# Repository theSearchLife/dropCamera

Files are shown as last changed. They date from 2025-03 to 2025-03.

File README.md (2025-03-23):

# Hardware

## Burnwire mechanism

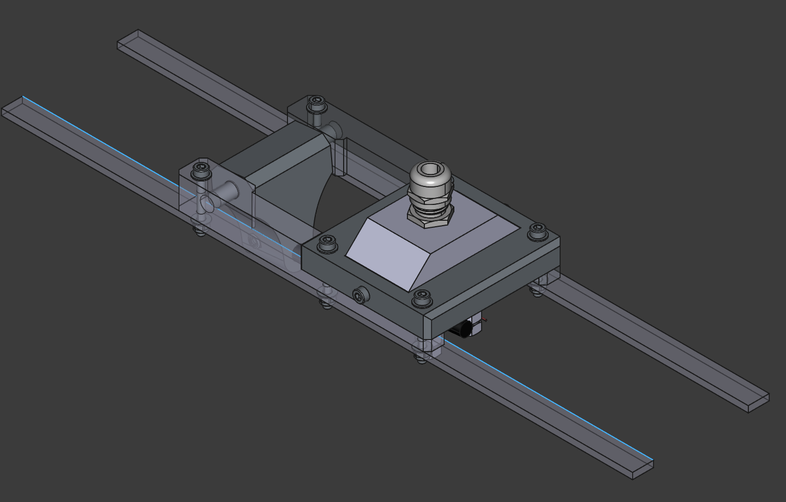
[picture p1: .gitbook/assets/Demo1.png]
Demo

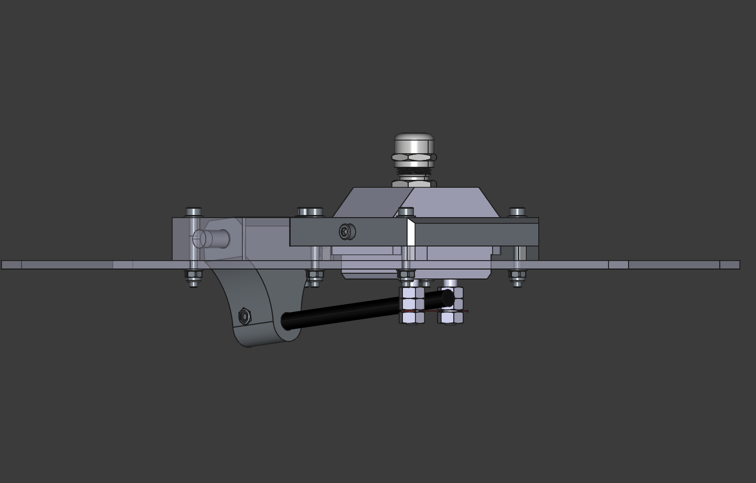
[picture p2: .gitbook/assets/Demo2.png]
Demo

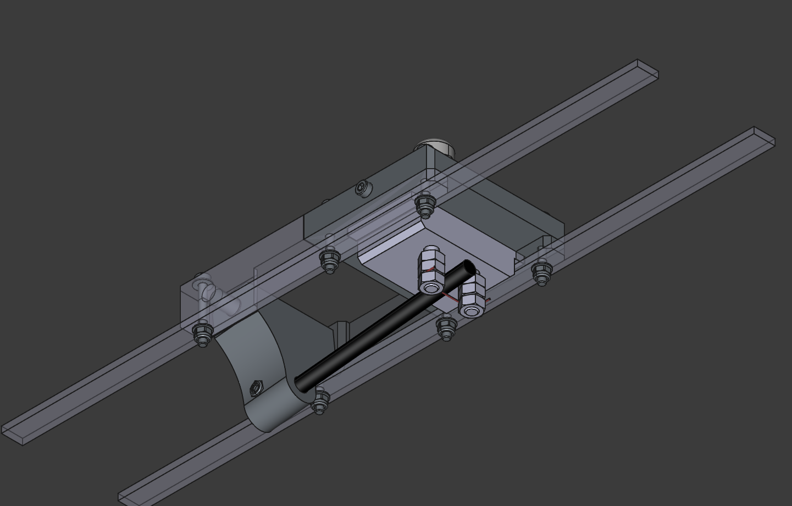
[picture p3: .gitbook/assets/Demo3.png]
Demo

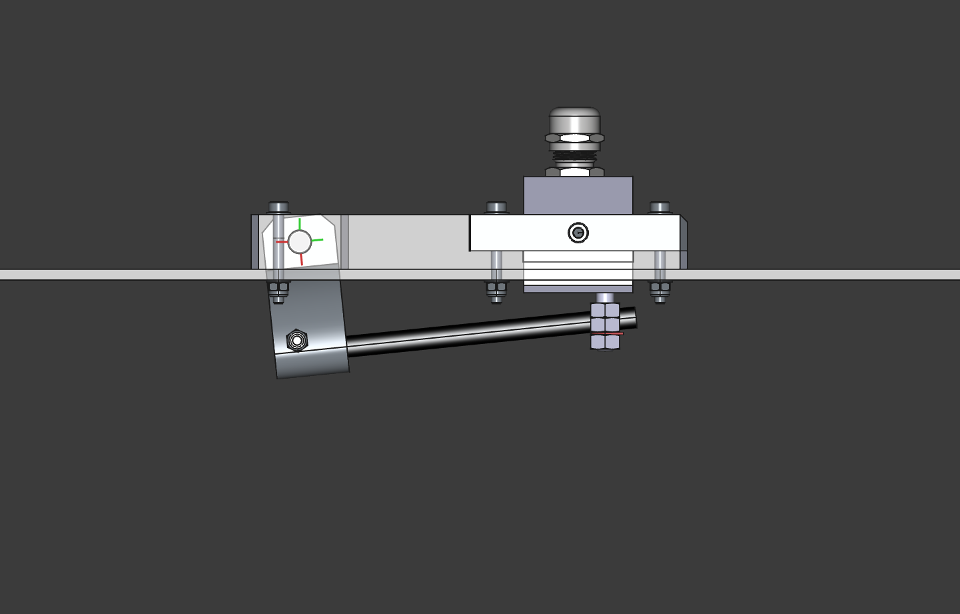
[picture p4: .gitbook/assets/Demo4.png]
Demo

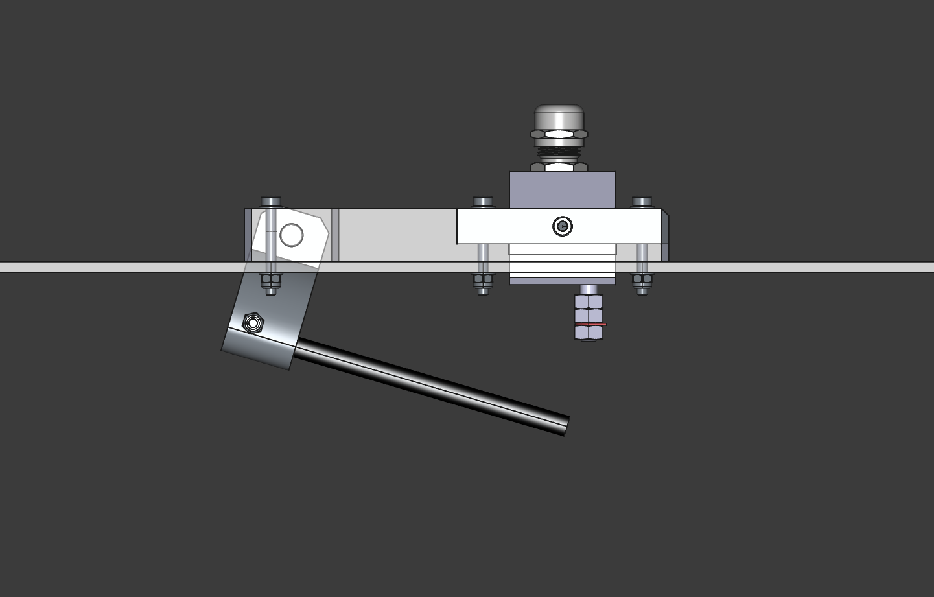
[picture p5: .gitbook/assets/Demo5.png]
Demo


### Hardware BOM

**All rods and fasteners must be stainless steel 316/A4**

* Rod 6x55mm
* Rod 6x70mm
* M12 Cable gland
* 2x Ring terminals
* 2x M5x25 ISO4017, [DIN 933 ](https://accu-components.com/us/full-thread-hexagon-bolts/19162-SEBF-M5-25-A4)  Screw (Hexagon head)
* 8x M5 nut [DIN 934](https://accu-components.com/us/hexagon-nuts/7910-HPN-M5-A4)
* 2x M5 [Star Washer](https://accu-components.com/us/external-fine-tooth-locking-washers/63131-HLFW-M5-A4)
* 7x M3 [DIN 985](https://accu-components.com/us/hexagon-nylon-locking-nuts/7957-HNN-M3-A4) (Nylon lock nut)
* 2x M3 nut [DIN 934](https://accu-components.com/us/hexagon-nuts/7907-HPN-M3-A4)
* 12x M3 Washer [DIN 125](https://accu-components.com/us/metric-flat-washers/72508-HPW-M3-A4)
  * Optional replace 6x M3 spring washers [DIN127B](https://accu-components.com/us/rectangular-profile-spring-washers/62558-HRSW-M3-A4)
* 2x M3x10 [DIN 912](https://accu-components.com/us/metric-cap-head-screws/3975-SSCF-M3-10-A4), DIN7984 or ISO4762 (Socket Head)
* M3x12 [DIN 912](https://accu-components.com/us/metric-cap-head-screws/3976-SSCF-M3-12-A4), DIN7984 or ISO4762 (Socket Head)
* 6x M3x25 [DIN 912](https://accu-components.com/us/metric-cap-head-screws/642040-SSCF-M3-25-A4), DIN7984 or ISO4762 (Socket Head)

* Nichromium wire

### 3D printing 

**Parts**
* BurnwireHolder
* BurnwireHolderSlot
* Gimbal
* GimbalHolder
* GimbalHolder (Mirror)

**3D printing orientation**
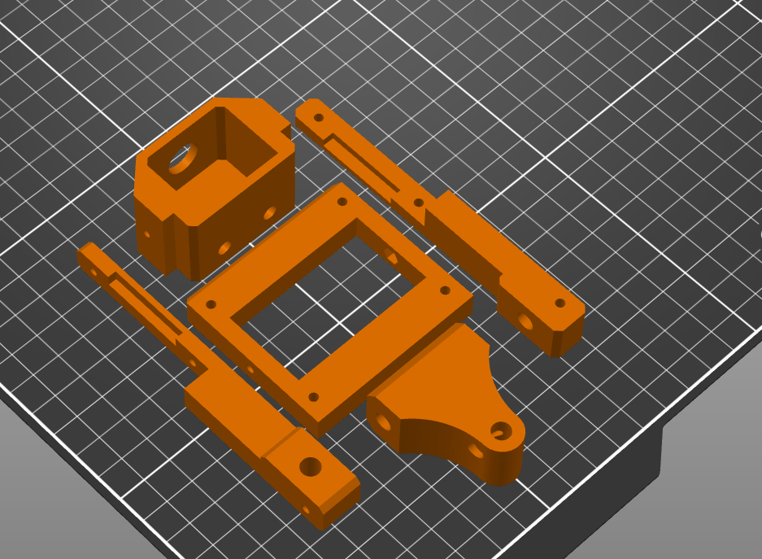
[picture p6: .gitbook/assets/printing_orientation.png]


**Printing Instructions**
* 100% infill
* Materials - Before choosing material, ensure your printed can print it. 
  * [PC blend](https://www.prusa3d.com/product/prusament-pc-blend-natural-970g/#printing-setup)
  * [ASA](https://www.prusa3d.com/product/prusament-asa-natural-850g/)
  * PETG

### Assembly

**All printed parts should be coated in waterproofing material**
Good choices would be [dichtol AM Hydro](https://diamant-polymer.de/en/shop/dichtol/am-hydro/), epoxy, other specialized coats for 3D printing.

**Prepare mounting holes on the steel beams** Use drill template provided to punch mark drill holes. Shorter side is where Nichromium wire will be placed. 
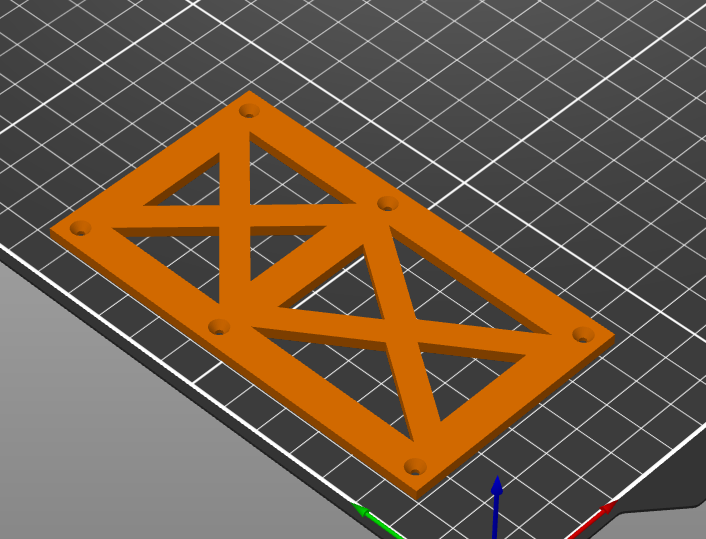
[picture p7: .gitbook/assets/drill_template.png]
drill template
 

1. Make key cutout on 100mm rod. 5mm from the end, 4mm wide.
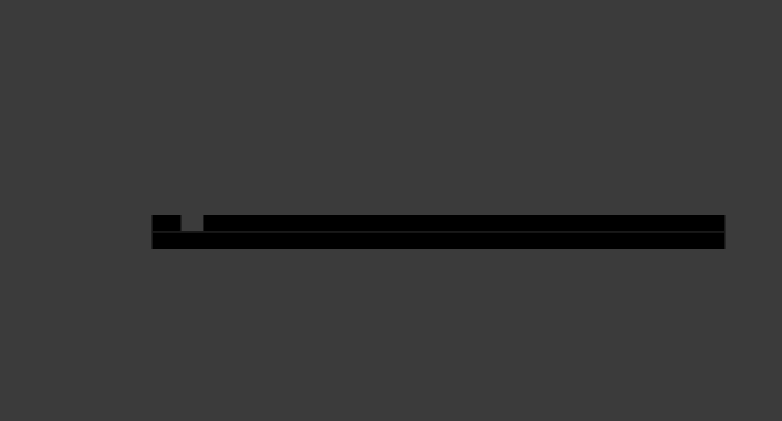
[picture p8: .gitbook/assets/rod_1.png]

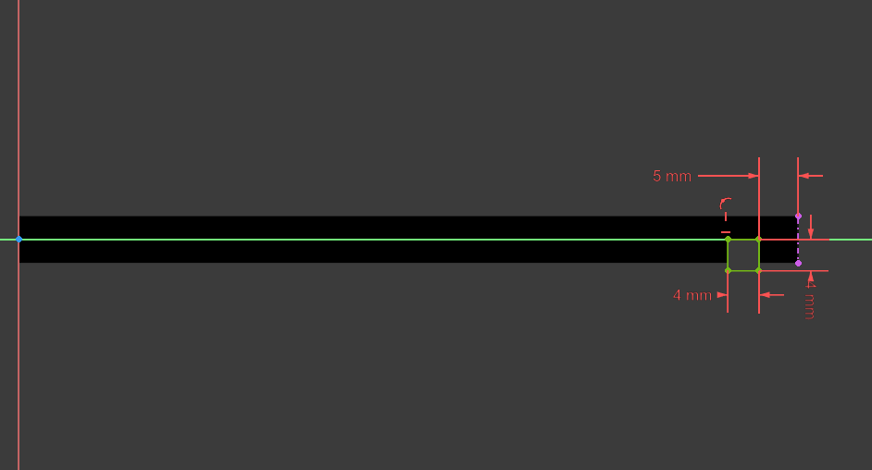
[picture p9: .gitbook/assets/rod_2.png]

2. Assemble Gimbal
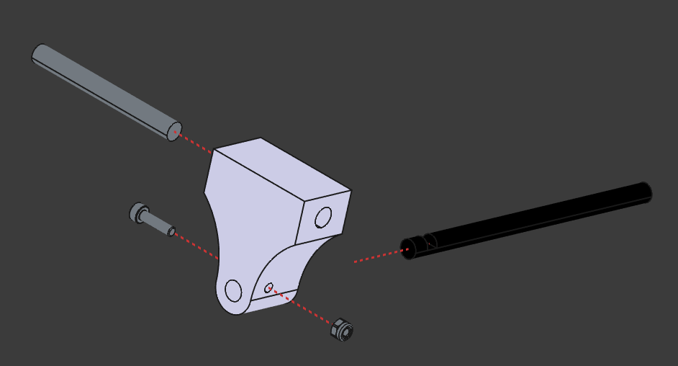
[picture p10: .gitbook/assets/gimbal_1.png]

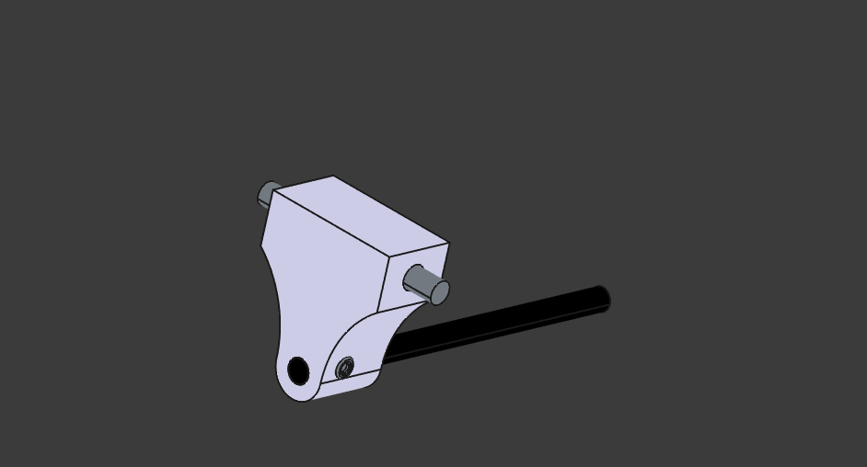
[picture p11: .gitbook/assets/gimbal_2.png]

    1. Insert 100mm rod with a cutout facing up, towards the screw hole.
    2. Fix it with M3x12 and nylon nut
    3. Insert 55m rod
3. Mount GimbalHolders and BurnWireHolderSlot
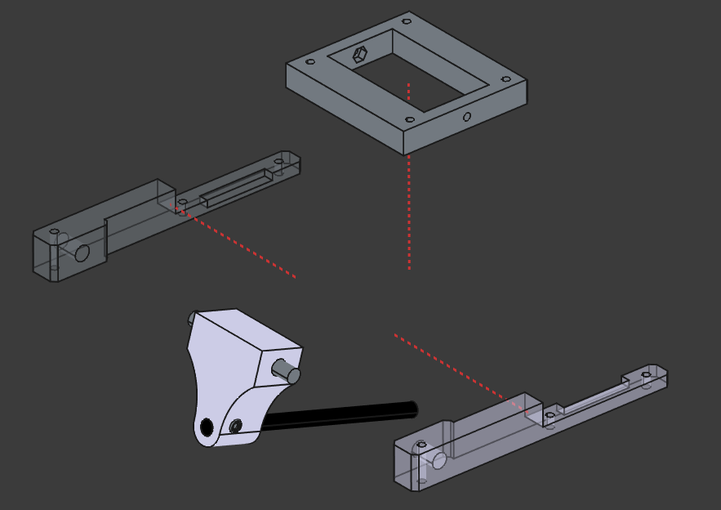
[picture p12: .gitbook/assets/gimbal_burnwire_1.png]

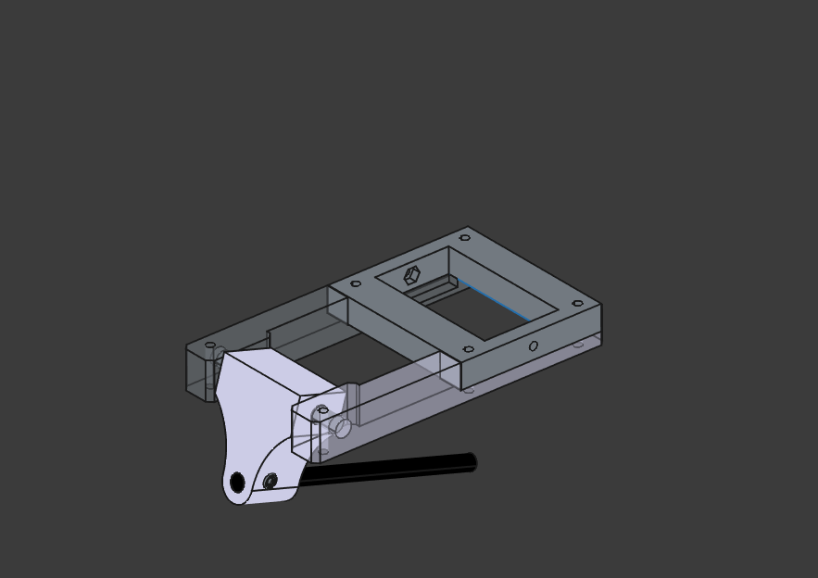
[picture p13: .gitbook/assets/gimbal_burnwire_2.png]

4. Fix it to the steel beams using M3x25 screws, washers and nylon locknuts. Ensure that washers have contact with 3D printed part. For metal surface it could be used a spring or starwasher to lock it in place.
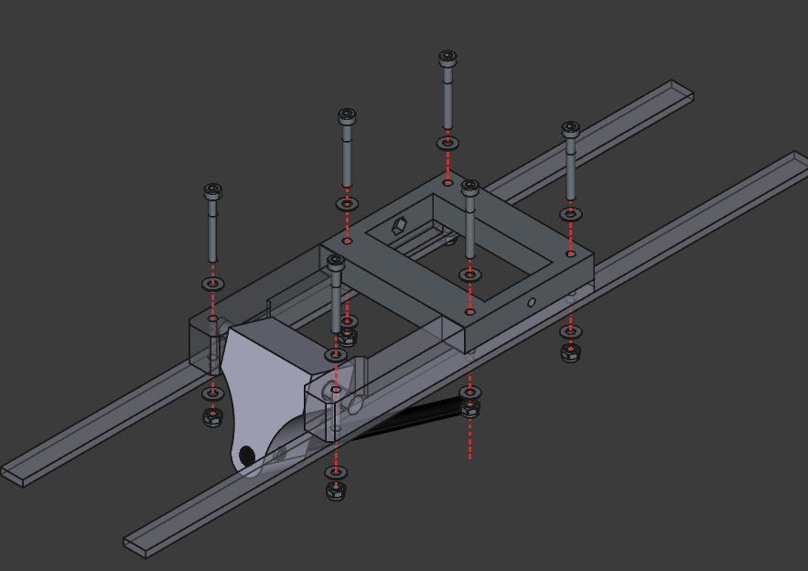
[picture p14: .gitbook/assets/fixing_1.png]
fixing

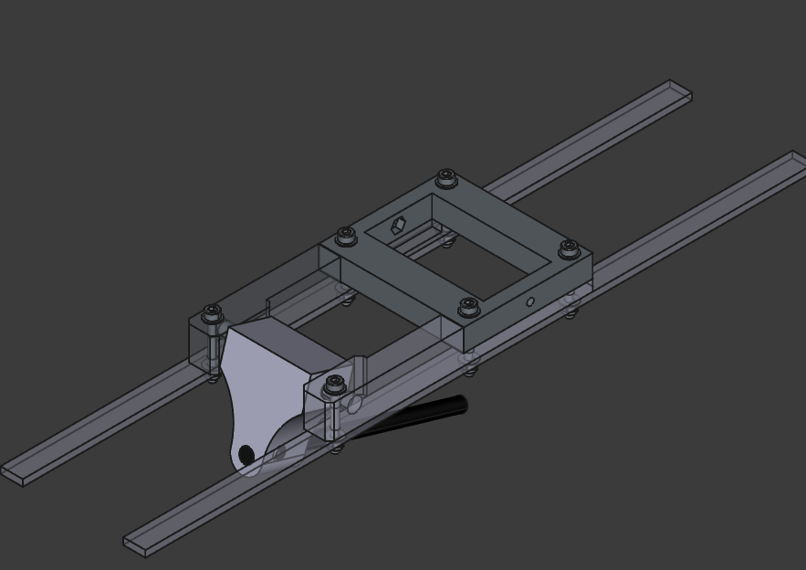
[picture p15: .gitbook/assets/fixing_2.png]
fixing

5. Insert 2x M3 nuts to the BurnWireHolderSlot
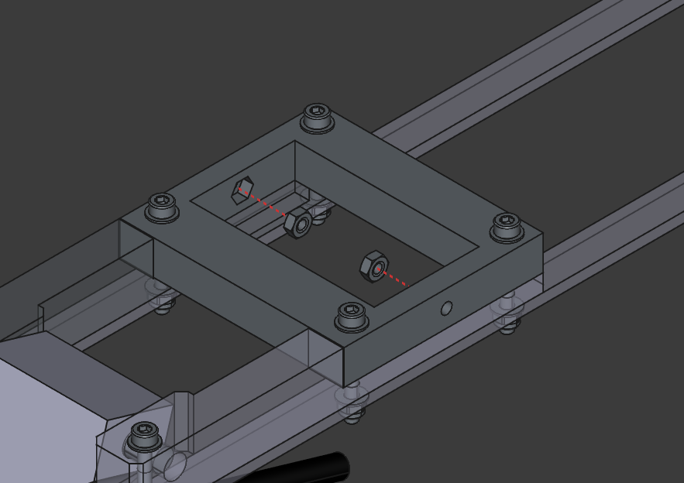
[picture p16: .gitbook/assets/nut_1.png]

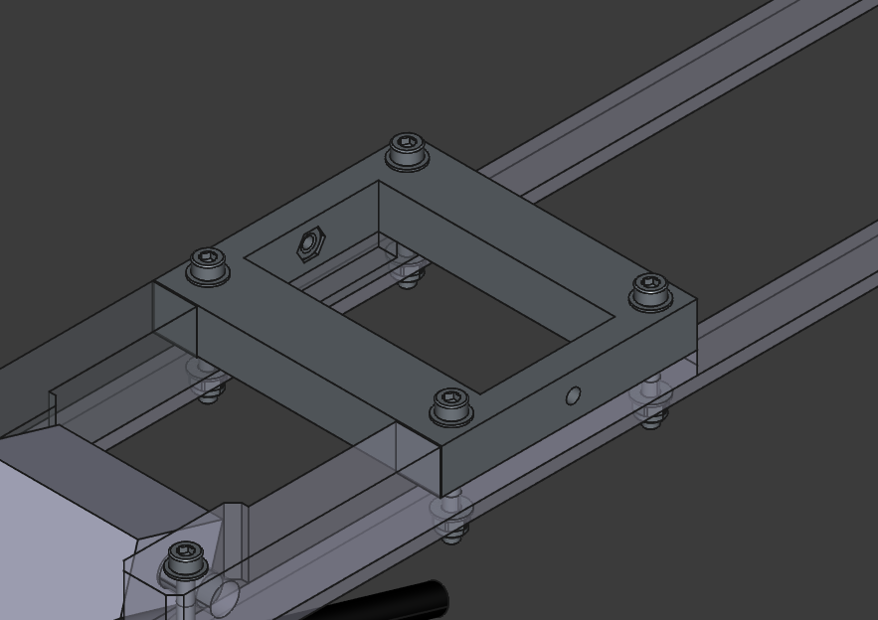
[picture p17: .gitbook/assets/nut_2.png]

6. **Crimp the cable to the ring terminal** !!!
7. Prepare 2x ring terminal stacks. Make it **tight**. In oder:
    1. Screw
    2. Ring terminal
    3. Star washer (not regular washer), for better contact/conductivity.
    4. Nut
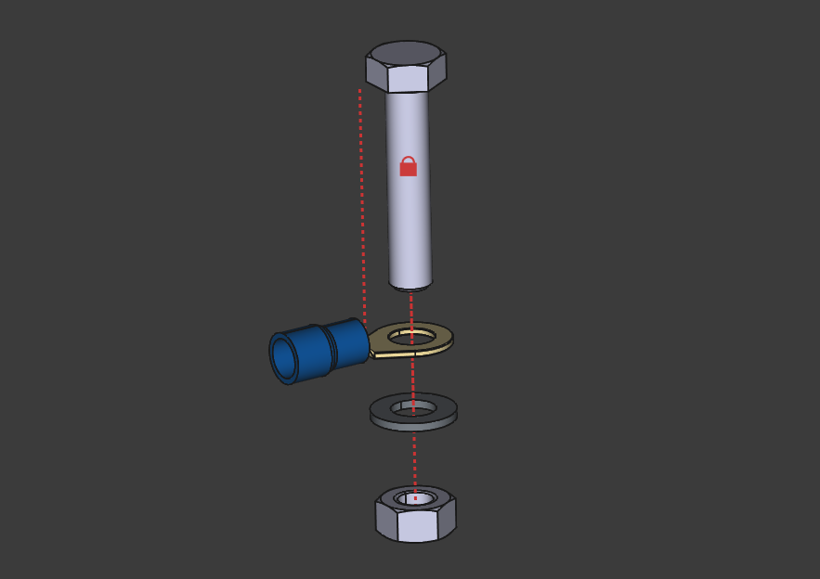
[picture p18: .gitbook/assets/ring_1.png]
ring

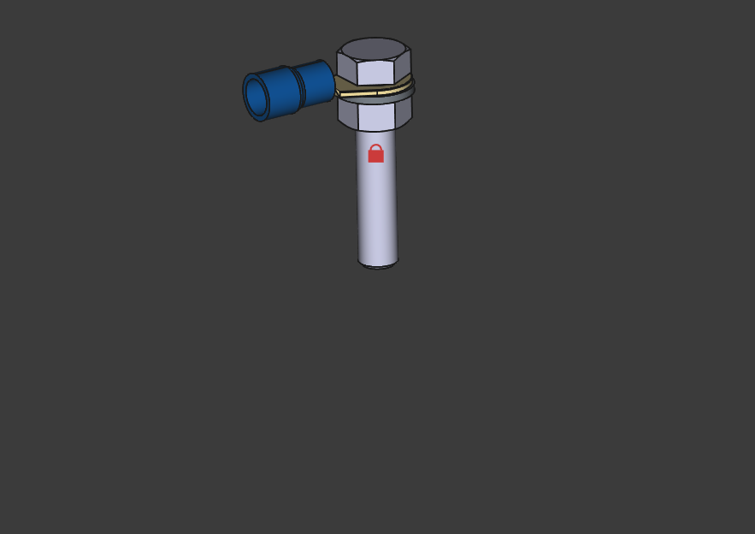
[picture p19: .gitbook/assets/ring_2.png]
ring

8. BurnwireHolder Assembly
    1. Insert ring terminal stack into the BurnwireHolder
    2. Lock it with nuts.
    3. Insert Cable gland
    4. Pass cable via cable gland. 
    5. Fill/seal it with epoxy resing. It could be mixed with glass fiber shreddings for extra strength.
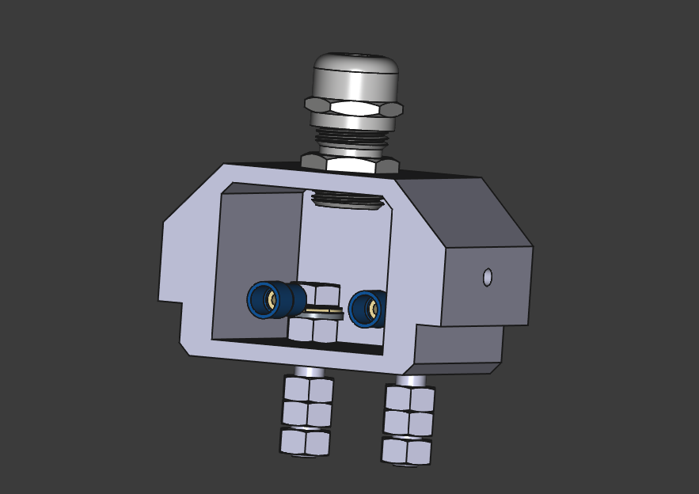
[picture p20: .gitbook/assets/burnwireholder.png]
burnwire

2 out of 3 nuts at the outside of the casing should be locked in together. They can be either touching the casing or not. The last most bottom nut should be used for locking in the burn wire.
9. Insert BurnwireHolder assembly into the slot
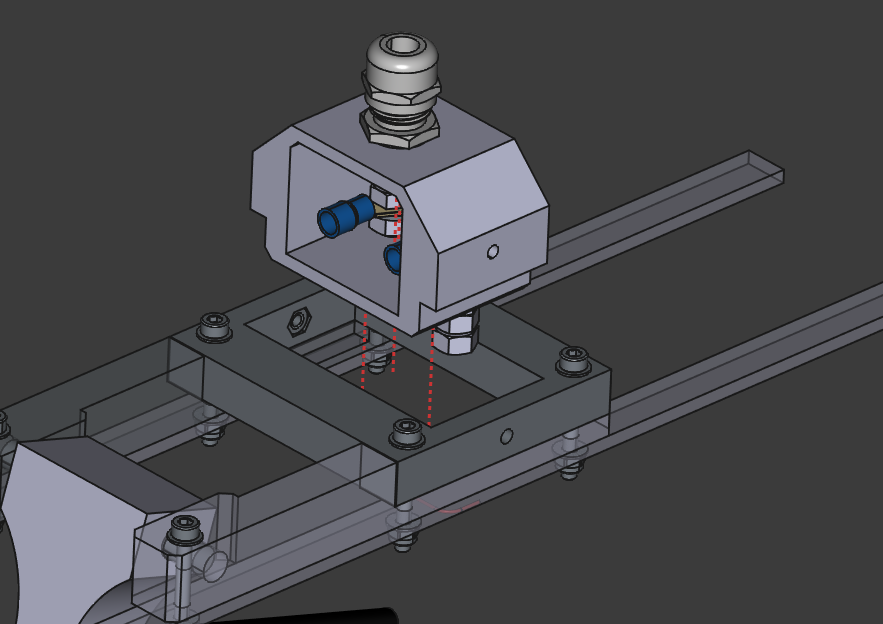
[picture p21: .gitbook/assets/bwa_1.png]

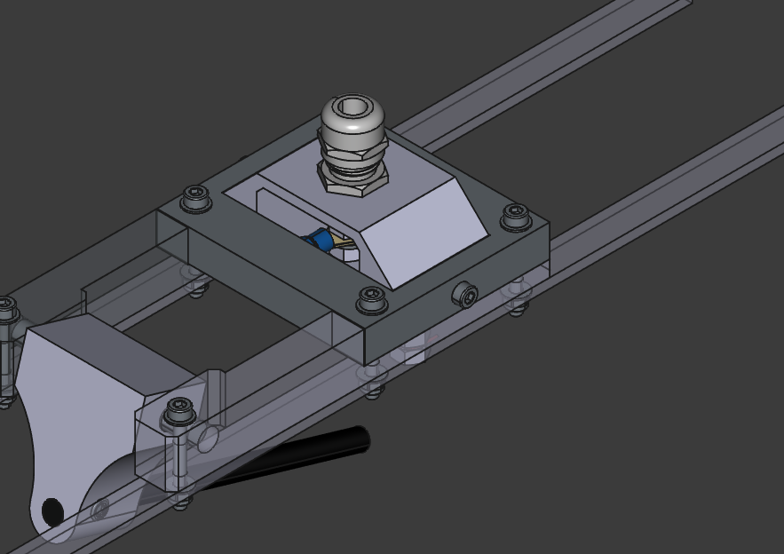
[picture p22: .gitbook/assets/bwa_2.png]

10. Fix the burnwireholder with 2x M3x10 screws
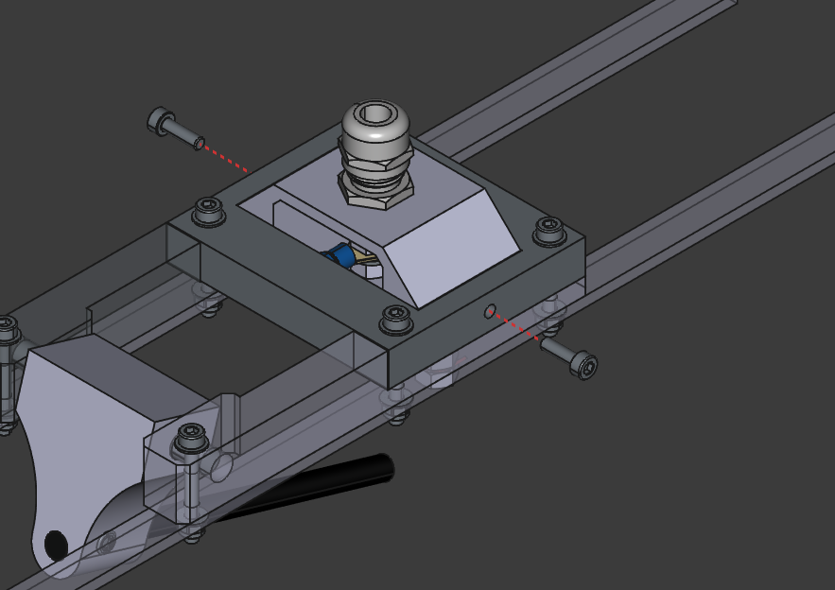
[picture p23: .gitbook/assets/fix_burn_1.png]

11. Load the burn wire
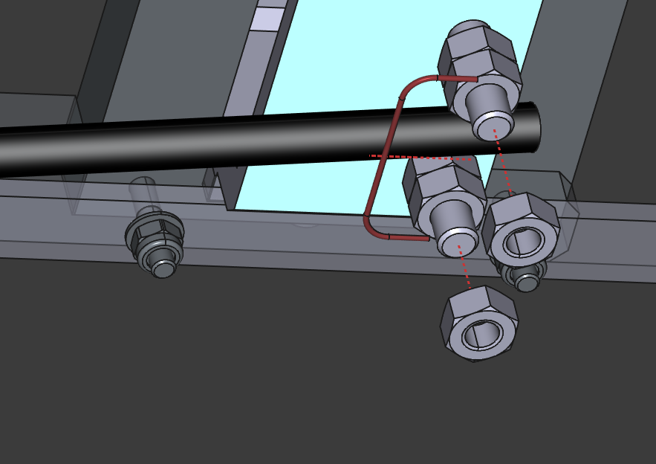
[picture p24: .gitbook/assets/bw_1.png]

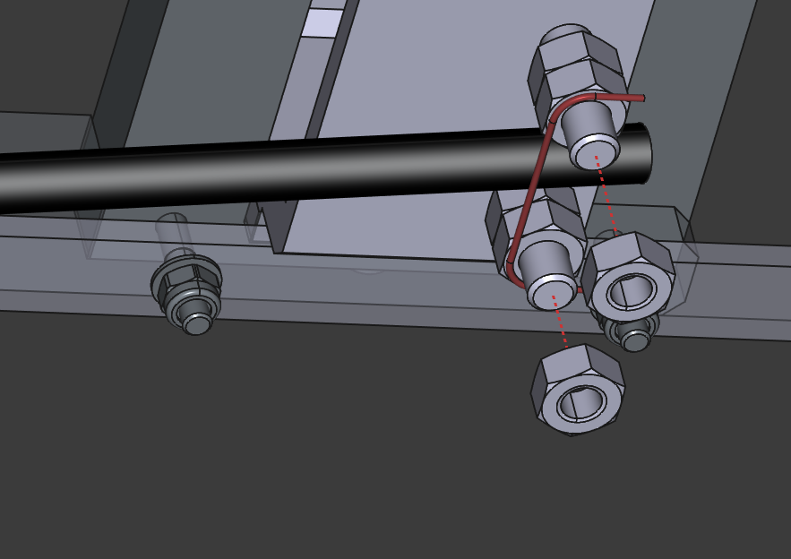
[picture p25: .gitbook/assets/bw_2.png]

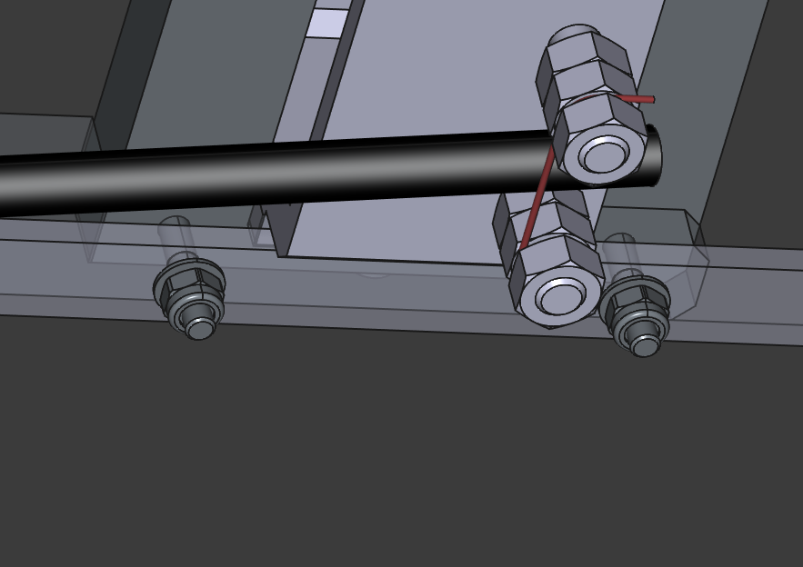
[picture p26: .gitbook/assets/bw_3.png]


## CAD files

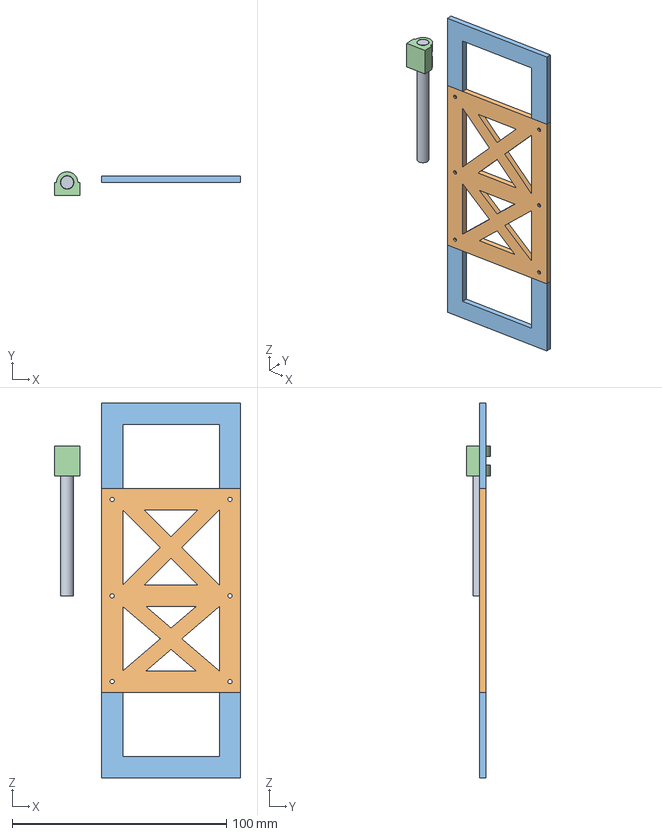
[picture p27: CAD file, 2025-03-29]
hardware/burnwire_setup_v5_2.FCStd
87.0 x 11.0 x 175.0 mm
Rod_100mm
DrillTemplate
SteelDemo
RodCutMarker

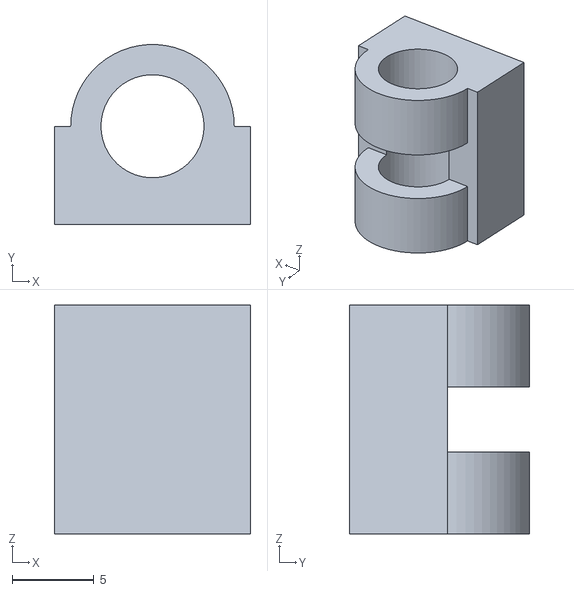
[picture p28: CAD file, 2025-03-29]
hardware/stl/burnwire_setup_v5_2-RodCutMarker (Meshed).stl
12.0 x 11.0 x 14.0

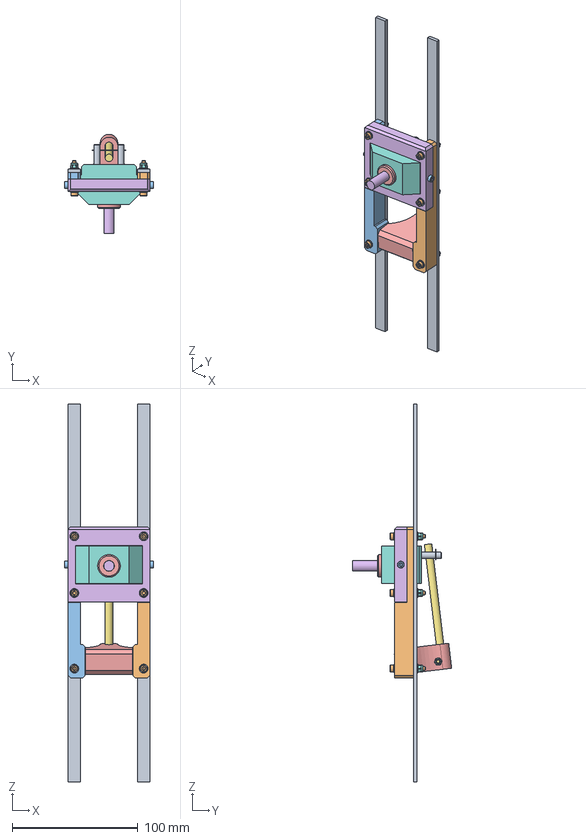
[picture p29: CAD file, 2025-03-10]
hardware/burnwire_setup_v5.FCStd
71.0 x 78.9 x 300.0 mm
SteelBeam x 2
GimbalHolder
GimbalHolder (Mirror #1)
Rod_55mm
Gimbal
BurnWireHolderSlot
Rod_100mm
BurnWireHolder
M5x25-Screw x 2
Ring Terminal003 x 2
Ring Terminal004 x 2
M5-Washer x 2
M5-Nut x 2
nichromiumWire
M3x12-Screw
M3-Nut x 7
M3-Washer x 12
M3x25-Screw x 6
M3x10-Screw x 2
M3-Nut008 x 2
CableGrip
Cable

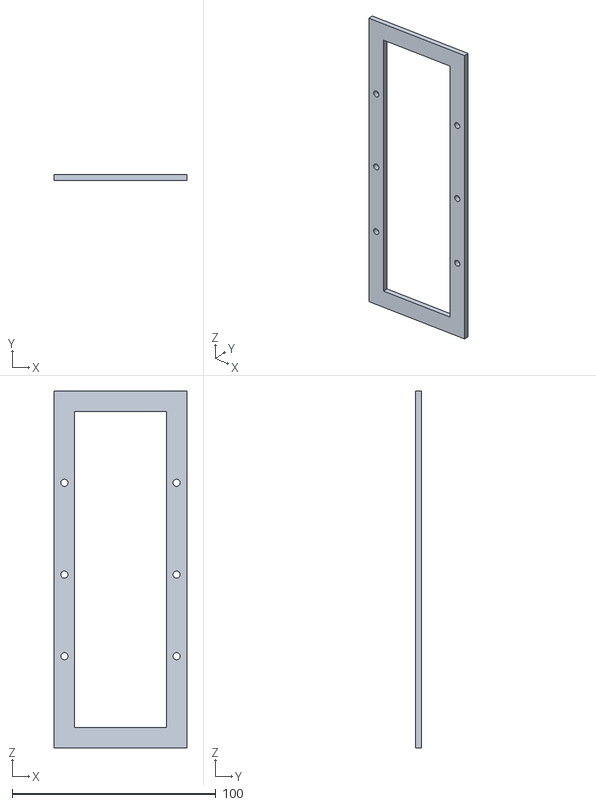
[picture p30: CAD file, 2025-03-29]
hardware/stl/burnwire_setup_v5_2-SteelDemo (Meshed).stl
65.0 x 3.00 x 175.0

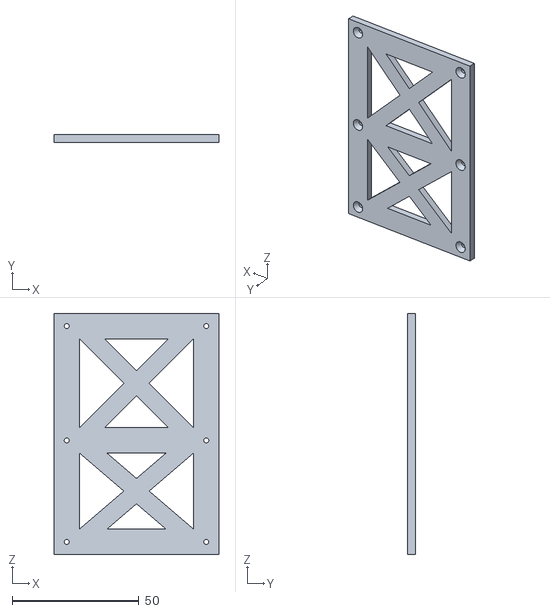
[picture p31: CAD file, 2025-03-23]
hardware/stl/burnwire_setup_v5_2-DrillTemplate (Meshed).stl
65.0 x 3.00 x 95.0

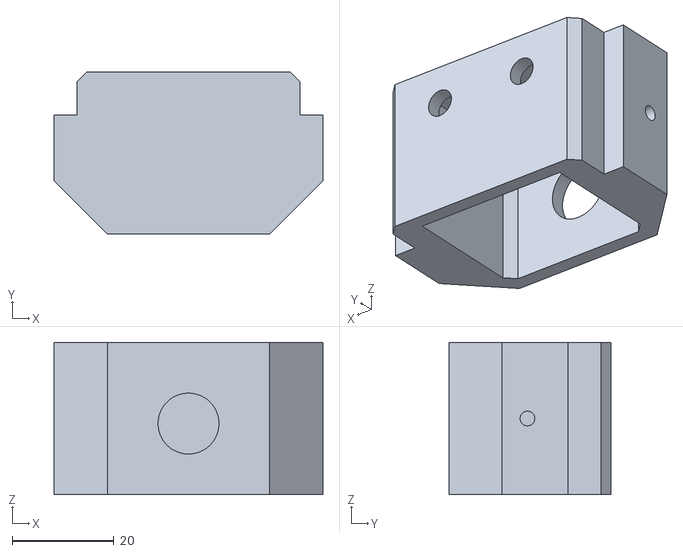
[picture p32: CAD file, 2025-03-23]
hardware/stl/burnwire_setup_v5_2-BurnWireHolder (Meshed).stl
53.0 x 32.0 x 30.0

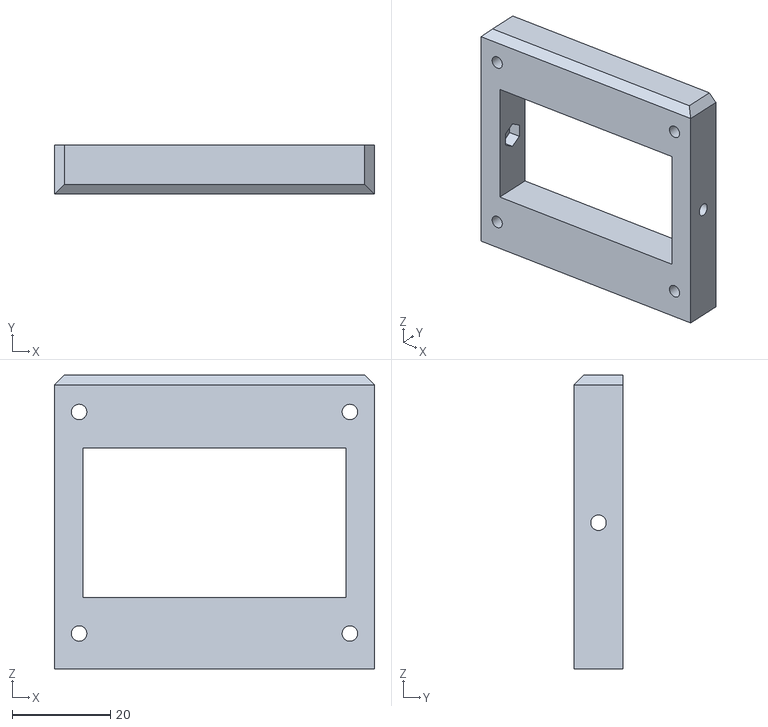
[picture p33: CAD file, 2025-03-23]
hardware/stl/burnwire_setup_v5_2-BurnWireHolderSlot (Meshed).stl
65.0 x 10.0 x 59.7

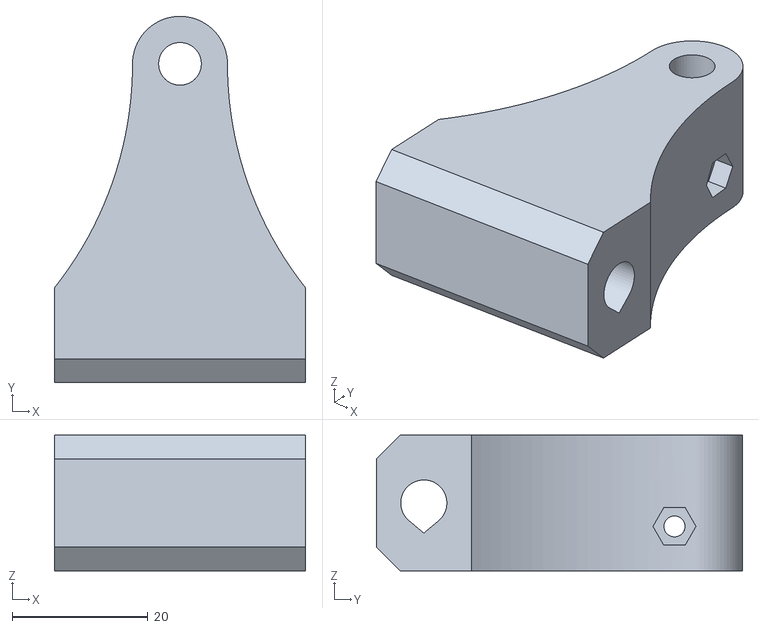
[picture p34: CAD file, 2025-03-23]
hardware/stl/burnwire_setup_v5_2-Gimbal (Meshed).stl
37.0 x 54.0 x 20.0

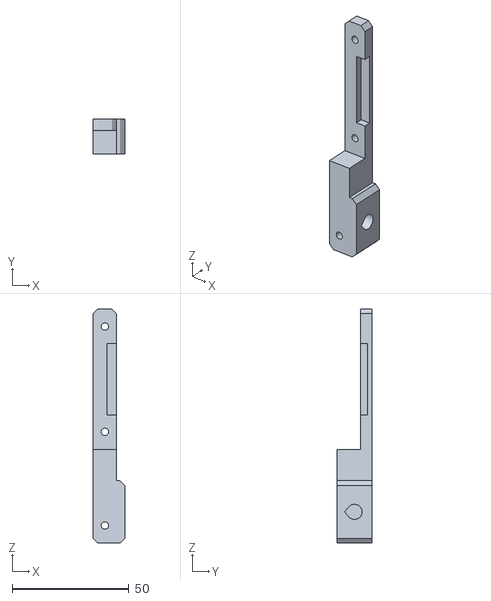
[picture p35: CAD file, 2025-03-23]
hardware/stl/burnwire_setup_v5_2-GimbalHolder (Mirror #1) (Meshed).stl
13.5 x 15.0 x 100.0

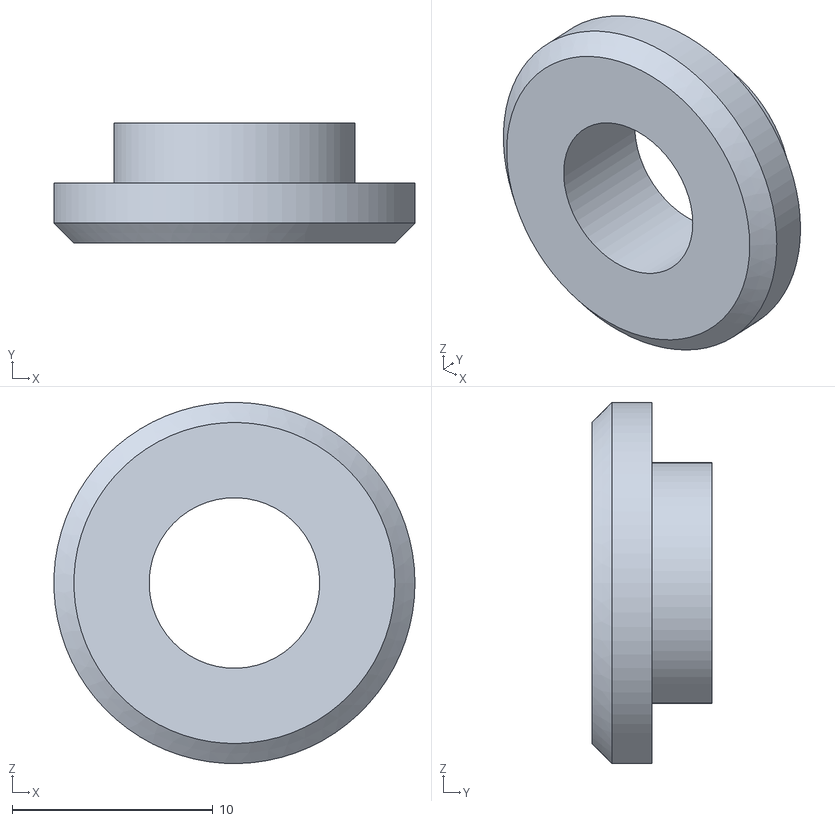
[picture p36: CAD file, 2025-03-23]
hardware/stl/burnwire_setup_v5_2-CableGrip (Meshed).stl
18.0 x 6.00 x 18.0

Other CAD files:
hardware/stl/burnwire_setup_v5_2-GimbalHolder (Meshed).stl

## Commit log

2025-03-03 added FreeCAD files
    [burnwire_setup_v5-BurnWireHolder (Meshed).stl, burnwire_setup_v5-BurnWireHolderSlot (Meshed).stl, burnwire_setup_v5-Gimbal (Meshed).stl, burnwire_setup_v5-Gimb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]
2025-03-03 documentation start
    [burnwire_setup_v5.FCStd]
2025-03-03 documentation added
    [burnwire_setup_v5-DrillTemplate (Meshed).stl, burnwire_setup_v5.FCStd]
2025-03-10 Added version with 70mm rod
    [burnwire_setup_v5.FCStd, burnwire_setup_v5_2.FCStd]
2025-03-23 updated STLs
    [burnwire_setup_v5-BurnWireHolder (Meshed).stl, burnwire_setup_v5-BurnWireHolderSlot (Meshed).stl, burnwire_setup_v5-DrillTemplate (Meshed).stl, burnwire_setup_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]
2025-03-23 added drill template
    [burnwire_setup_v5_2-DrillTemplate (Meshed).stl, burnwire_setup_v5_2.FCStd]
2025-03-29 added jigs
    [burnwire_setup_v5_2-RodCutMarker (Meshed).stl, burnwire_setup_v5_2-SteelDemo (Meshed).stl, burnwire_setup_v5_2.FCStd]
